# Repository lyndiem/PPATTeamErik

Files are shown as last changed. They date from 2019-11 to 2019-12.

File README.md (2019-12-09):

# PPATTeamErik
This is a collection of all files needed to make a hinged wedge assistive mounting device for wheelchair boarding. These are Solidworks 2018 files and require Solidworks 2018 or later to open. The part files for the components that need to be 3D Printed or machined are additionally attached directly in the Instructable https://www.instructables.com/id/PPAT-Team-Erik/. 

STEP versions of all parts and assemblies can be found at PPATTeamErik/FilesForInstructable/STEP Files For Documentation, and are linked throughout the Instructable. These STEP files are compatible with other versions of CAD and are backwards compatible with Solidworks.

Explanations of the purposes of each part, how it is made, and suggestions for modifications are included in each step of the Instructable. Directions for assembly are included at the end of the Instructable and below.
1. Using the Arbor Press, press one 7.5" long shaft through the 1/2" diameter holes in a 3D printed hinged wedge such that the wedge is centered on the shaft (extending 1.5" on both sides).
2. Slide one aluminum mounting plate onto each end of the shaft.
3. Attach shaft collar outside the aluminum mounting plates on each end of the shaft.
4. Tighten the set screws.
5. Repeat steps 1-4 for the second hinged wedge.

6. Cut 2 L-brackets to 7.5" length
7. Measure and drill appropriate holes for mounting each L-bracket to the board
8. Place the bottom of the L below the board and align the holes
9. Place screws through each hole in the board
10. Attach a locknut on the end of each screw and loosely tighten (do not fully tighten until all locknuts have been placed).
11. Apply a drop of Loctite to the threads of each screw.
12. Tighten the locknut fully and let it dry.
13. Align the component assembly to the board so that the aluminum mounting plates rest on the top of the L-brackets and align with the mounting holes.
14. Drill appropriate holes for mounting the component assembly to the board with the aluminum mounting plates resting on the top of the L-brackets
15. Place one screw through each hole of the mounting plates
16. Attach a locknut on the end of each screw and loosely tighten (do not fully tighten until both locknuts have been placed).
17. Apply a drop of Loctite to the threads of each screw.
18. Tighten the locknut fully and let it dry.
19. Repeat steps 8-18 for the second hinged wedge.

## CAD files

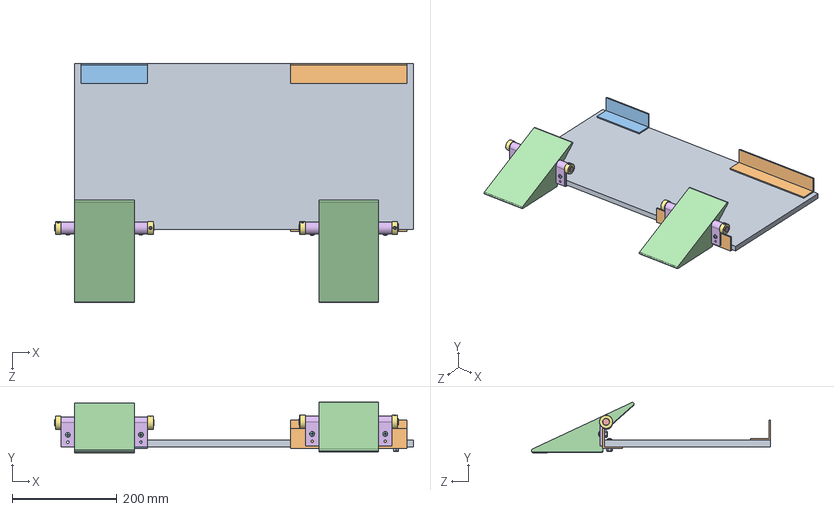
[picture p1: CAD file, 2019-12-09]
Assemblies/Board_HingedWedge_Assembly.SLDASM
685.8 x 96.6 x 456.9 mm
Board base
L-Bracket long x 2
L-Bracket short x 2
HingedWedge3DPrint x 2
Shaft x 2
AluminumPlate x 4
9946K150_SET SCREW SHAFT COLLAR x 4
91772A242_18-8 SS PAN HEAD PHILLIPS MACHINE SCREW x 5
91831A011_TYPE 18-8 STAINLESS STL NYLON-INSERT LOCKNUT x 5

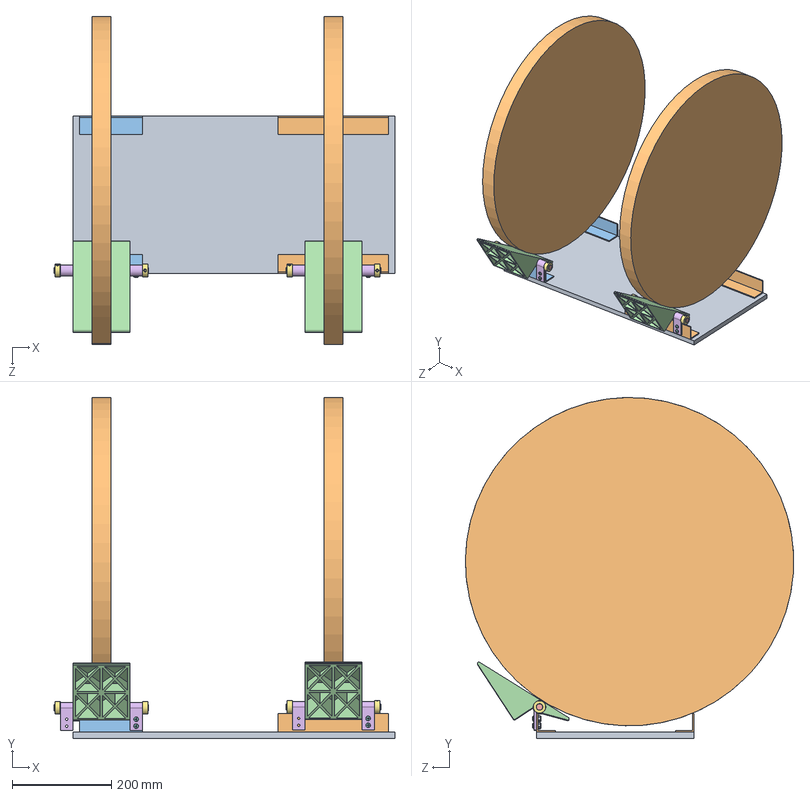
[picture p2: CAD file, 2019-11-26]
Assemblies/RaisedMount.SLDASM
685.8 x 685.9 x 660.1 mm
Board base
L-Bracket long x 2
L-Bracket short x 2
HingedWedge3DPrint x 2
Shaft x 2
AluminumPlate x 4
9946K150_SET SCREW SHAFT COLLAR x 4
91772A242_18-8 SS PAN HEAD PHILLIPS MACHINE SCREW x 4
91831A011_TYPE 18-8 STAINLESS STL NYLON-INSERT LOCKNUT x 4
wheelchair wheel x 2

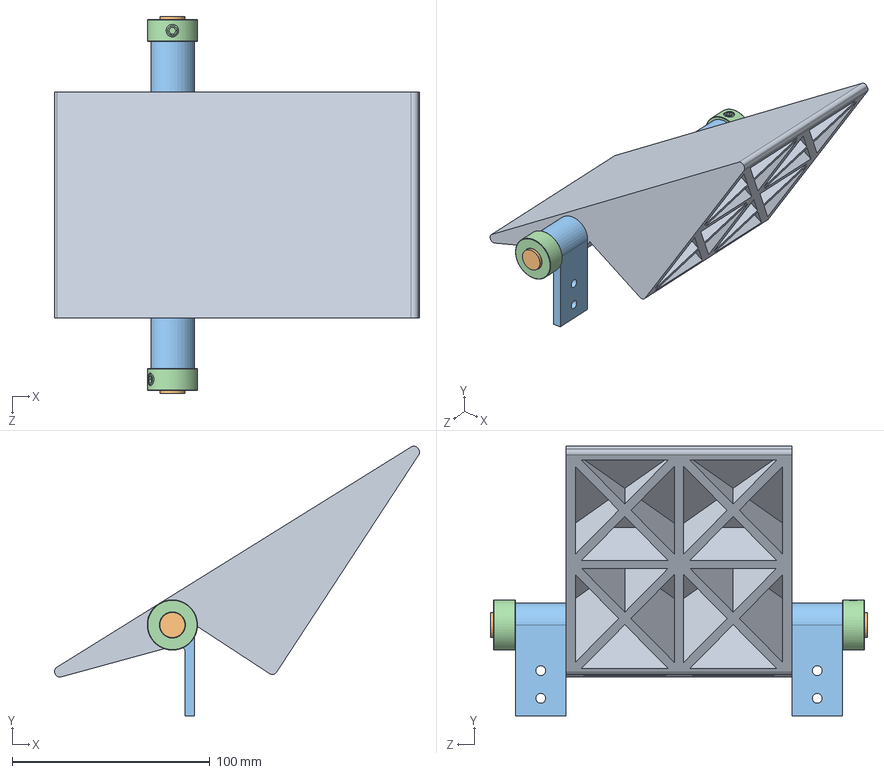
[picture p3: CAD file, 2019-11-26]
Assemblies/ComponentAssembly.SLDASM
184.4 x 136.3 x 190.5 mm
HingedWedge3DPrint
Shaft
AluminumPlate x 2
9946K150_SET SCREW SHAFT COLLAR x 2

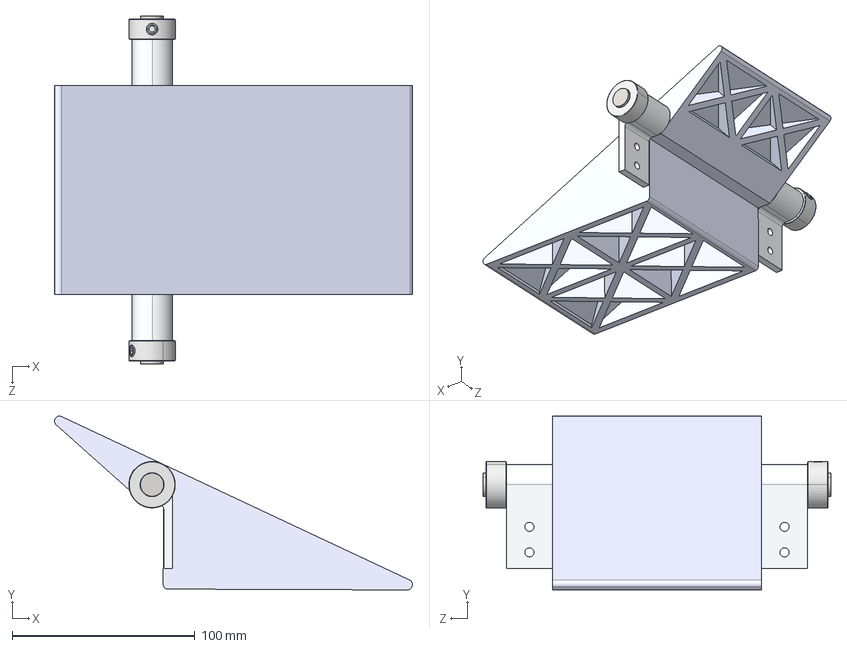
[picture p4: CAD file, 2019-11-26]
FilesForInstructable/STEP Files For Documentation/ComponentAssembly.STEP
196.0 x 95.2 x 190.5 mm

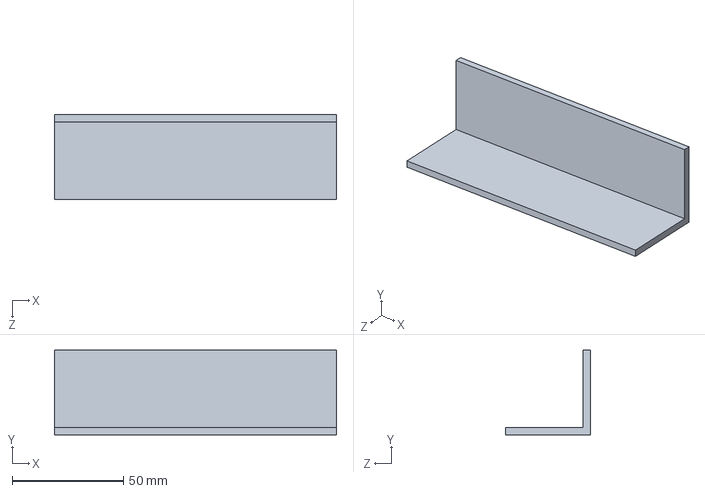
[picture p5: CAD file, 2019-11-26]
Assemblies/Files Needed for Assemblies/L-Bracket short.SLDPRT
127.0 x 38.1 x 38.1 mm

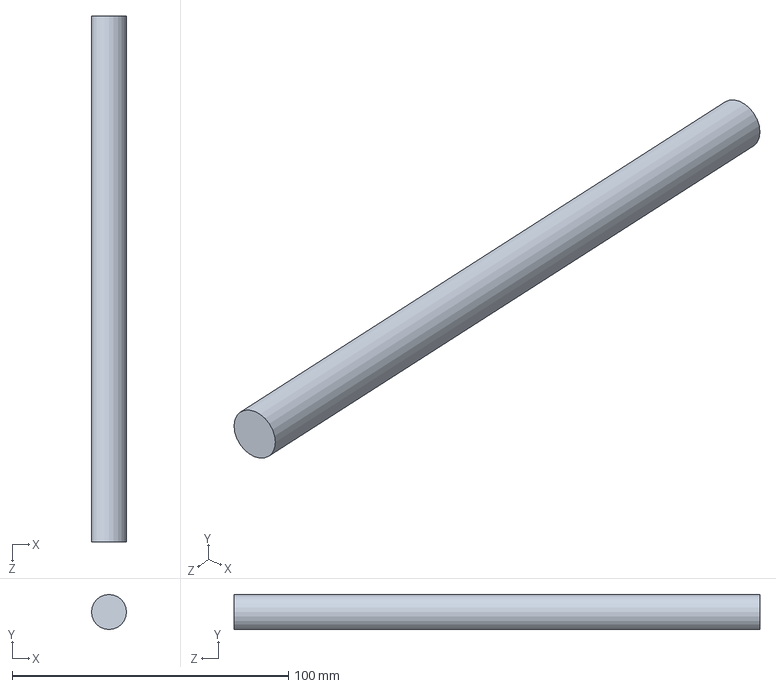
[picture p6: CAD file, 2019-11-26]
FilesForInstructable/Shaft.SLDPRT
12.7 x 12.7 x 190.5 mm

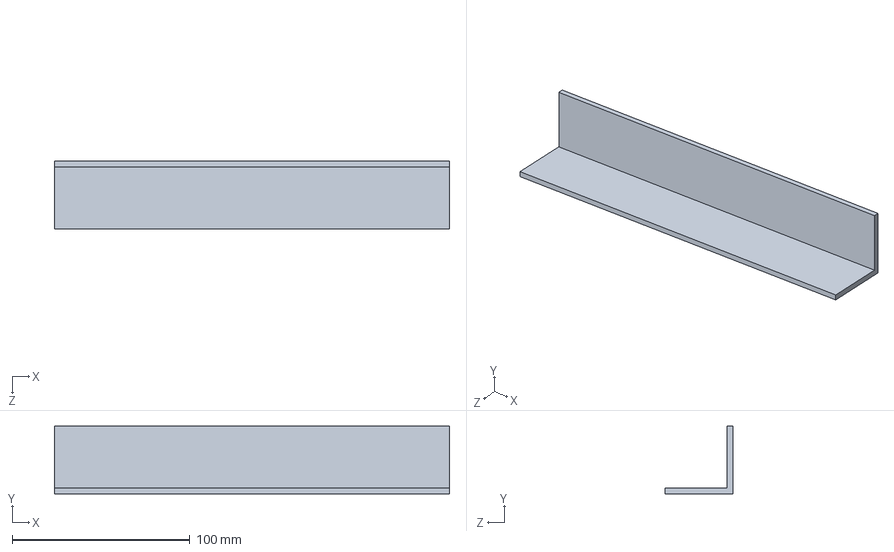
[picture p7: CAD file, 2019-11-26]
Assemblies/Files Needed for Assemblies/L-Bracket long.SLDPRT
222.2 x 38.1 x 38.1 mm

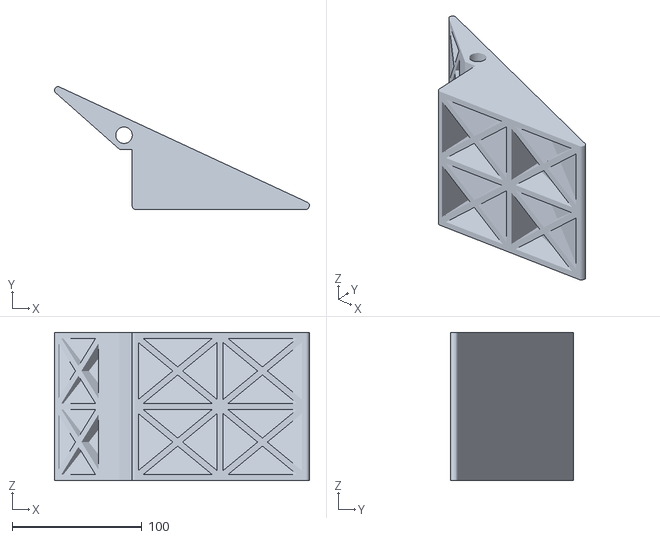
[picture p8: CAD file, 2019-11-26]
FilesForInstructable/HingedWedge3DPrint.STL
196.4 x 94.5 x 114.3

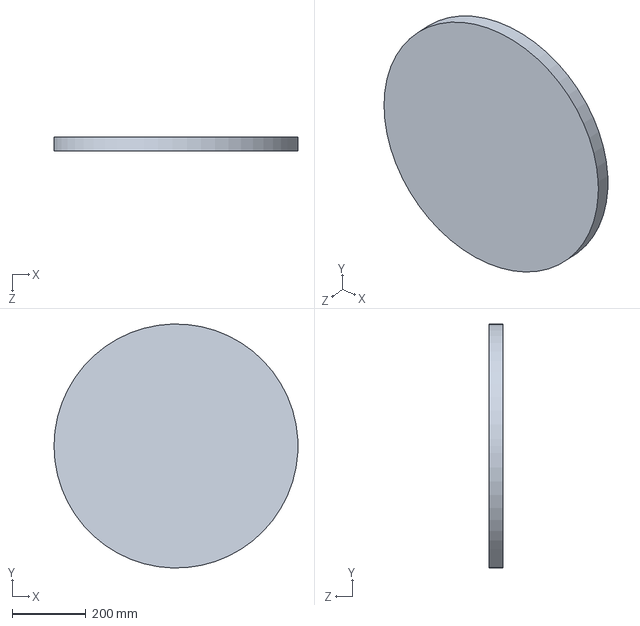
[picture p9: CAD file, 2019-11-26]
Assemblies/Files Needed for Assemblies/wheelchair wheel.SLDPRT
660.4 x 660.1 x 38.1 mm

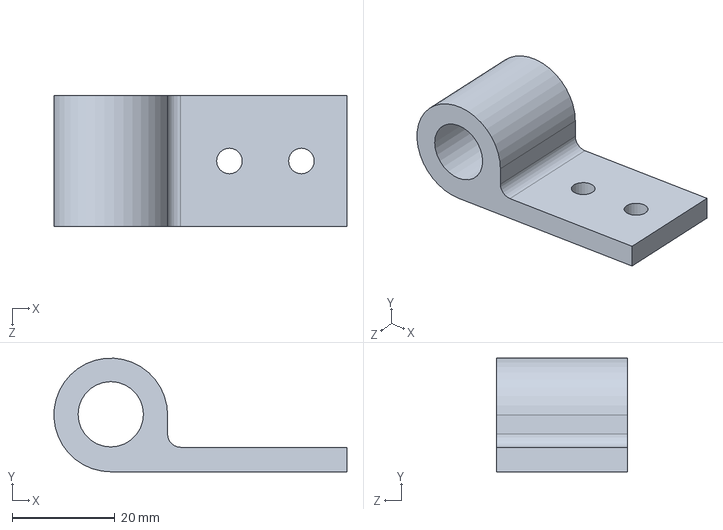
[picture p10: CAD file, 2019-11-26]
FilesForInstructable/AluminumPlate.SLDPRT
56.9 x 22.1 x 25.4 mm

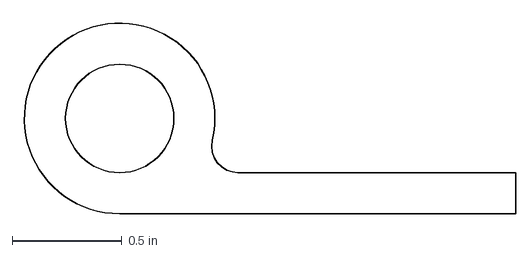
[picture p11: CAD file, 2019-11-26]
FilesForInstructable/dxf_waterjet.dxf
2.28 x 0.901 in

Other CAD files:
FilesForInstructable/STEP Files For Documentation/Board_HingedWedge_Assembly.STEP
FilesForInstructable/STEP Files For Documentation/L-Bracket long.STEP
FilesForInstructable/STEP Files For Documentation/wheelchair wheel.STEP
Assemblies/Files Needed for Assemblies/AluminumPlate.SLDPRT
FilesForInstructable/STEP Files For Documentation/L-Bracket short.STEP
Assemblies/Files Needed for Assemblies/91772A242_18-8 SS PAN HEAD PHILLIPS MACHINE SCREW.SLDPRT
Assemblies/Files Needed for Assemblies/91831A011_TYPE 18-8 STAINLESS STL NYLON-INSERT LOCKNUT.SLDPRT
Assemblies/Files Needed for Assemblies/9946K150_SET SCREW SHAFT COLLAR.SLDPRT
Assemblies/Files Needed for Assemblies/HingedWedge3DPrint.SLDPRT
FilesForInstructable/AluminumPlate.SLDDRW
FilesForInstructable/STEP Files For Documentation/91772A242_18-8 SS PAN HEAD PHILLIPS MACHINE SCREW.STEP
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
